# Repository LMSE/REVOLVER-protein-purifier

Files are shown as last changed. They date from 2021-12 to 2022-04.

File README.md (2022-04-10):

# REVOLVER: An automated protein purification system

<p align="center">
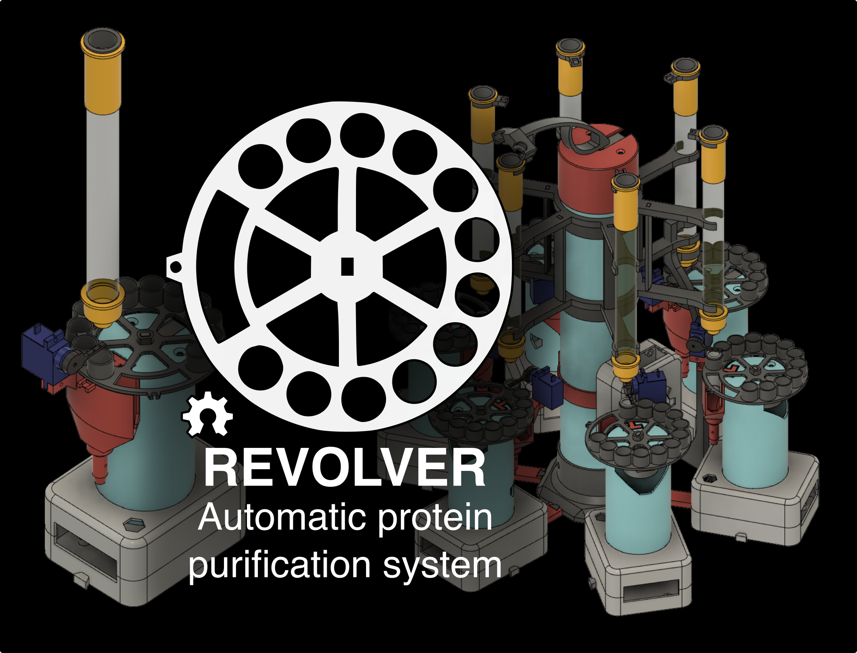
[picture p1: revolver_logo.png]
  
</p>

This repository contains all the hardware and firmware files to build and operate REVOLVER: an automated protein purifier based on paralleled large-scale gravity-column workflows. We also present MULTIVOLVER, a multiplexed version of REVOLVER that allows for simultaneous purification of up to six samples at a time.

REVOLVER was developed by Patrick Diep and Jose L. Cadavid at the University of Toronto. A full and detailed description of our system has been published in HardwareX and can be found [here](https://doi.org/10.1016/j.ohx.2022.e00291).

## Contents of repository

This repository contains all files necessary to print, build, and operate REVOLVER. It is divided in three main sections:

### Electronics

This folder contains the schematics for wiring the components of REVOLVER to an Arduino Nano board. This schematic was used to create a custom PCB using [EasyEDA](https://easyeda.com/) that was then ordered through [JLCPCB](https://jlcpcb.com/). The PCB file is included as a Gerber file that can be used to directly order a copy of the PCB (two PCBs fit a 10x10 cm panel). We additionally include a .json version of the PCB that can be opened with EasyEDA.

The raw PCB project can be accessed through [OSHWLab](https://oshwlab.com/JoseLCadavid/fractioncollector). If you would like to make your own PCB, please clone the project first and proceed with your improvements. Our current PCB corresponds to V2 in the project page.

### Firmware

This folder contains the Arduino firmware for configuring REVOLVER in single mode (single_sampler) or in MULTI-VOLVER mode (distributor_device and revolver_device). To upload (flash) the firmware to an Arduino board, you'll need a recent version of the Arduino IDE that can be found [here](https://www.arduino.cc/en/software). You can follow [this](https://www.arduino.cc/en/Tutorial/getting-started-with-ide-v2/ide-v2-uploading-a-sketch) tutorial on how to upload the firmware.

REVOLVER uses code and libraries written by other users and we would like to acknowledge them here:

* Serial communication and parser: This routine is based on [this](https://forum.arduino.cc/t/serial-input-basics-updated/382007/8) excellent tutorial by user **Robin2** on the Arduino forums.

* I2C bus scanner: This function is based on [this](https://playground.arduino.cc/Main/I2cScanner/) code.

Additionally, our code relies on these libraries:

* [Stepper](https://www.arduino.cc/en/reference/stepper/): For controlling stepper motors.
* [Servo](https://www.arduino.cc/reference/en/libraries/servo/): For controlling servos.
* [Wire](https://www.arduino.cc/en/reference/wire): For handling I2C communication.

Please verify that your Arduino IDE has access to these libraries before uploading the firmware to the Arduino boards. You can follow [this](https://www.arduino.cc/en/Guide/Libraries) tutorial for more information on how to do so. Detailed instructions on operating REVOLVER can be found in our manuscript.

### Hardware

This folder contains the STL files for all the 3D-printed parts required for REVOLVER and MULTI-VOLVER. These parts can be printed with no supports using any FDM printer with a size similar to that of an Ender 3; we've printed all our parts in PLA. We also included the f3d files that can be edited using Fusion 360 in case you'd like to customize the system even more. The bill of materials (BOM) is also included as a spreadsheet with some useful links to purchase parts.

## Building and using REVOLVER

The instructions for setting up and using REVOLVER are given in more detail in our manuscript. REVOLVER is controlled via serial commands, so any computer with a working USB connector and an installation of the Arduino IDE is required.

If you experience any issues when using our system, or otherwise have other suggestions, please create an issue and we are happy to help as soon as we can. Note that our manuscript includes a guide to troubleshooting common problems, so please check it out before posting.

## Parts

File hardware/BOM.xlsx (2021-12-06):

Designator | Components | Cost per package - CAD | Items per package | Items per REVOLVER | Total cost per REVOLVER (CAD) | Items per 3-device MULTIVOLVER | Total cost per 3-device MULTIVOLVER (CAD) | Items per 6-device MULTIVOLVER | Total cost per 6-device MULTIVOLVER (CAD) | Material Source | Material type
PURCHASED IN SETS
Servo | SG90 servo motor | $18.00 | 5 | 1 | $3.60 | 4 | $14.40 | 4 | $14.40 | https://www.amazon.ca/gp/product/B07Z16DWGW/ref=ppx_yo_dt_b_asin_title_o08_s00?ie=UTF8&psc=1 | Electronic Component
Servo horn | Single-sided horn for SG90 servo motor |  |  |  | cost included above |  | cost included above |  | cost included above | https://www.amazon.ca/gp/product/B07Z16DWGW/ref=ppx_yo_dt_b_asin_title_o08_s00?ie=UTF8&psc=1 | Metal
6 mm phillips screw | 6 mm phillips screw |  |  |  | cost included above |  | cost included above |  | cost included above | https://www.amazon.ca/gp/product/B07Z16DWGW/ref=ppx_yo_dt_b_asin_title_o08_s00?ie=UTF8&psc=1 | Metal
Stepper | 28BYJ-48 stepper motor with ULN2003 driver board | $20.00 | 5 | 1 | $4.00 | 3 | $12.00 | 3 | $12.00 | https://www.amazon.ca/gp/product/B087B5NWY4/ref=ppx_yo_dt_b_asin_title_o00_s00?ie=UTF8&psc=1 | Electronic Component
Stepper driver | ULN2003 (DIP-16L) Darlington array |  |  |  | cost included above |  | cost included above |  | cost included above | https://www.amazon.ca/gp/product/B087B5NWY4/ref=ppx_yo_dt_b_asin_title_o00_s00?ie=UTF8&psc=1 | Electronic Component
HARDWARE
PLA filament | EconoFil™ PLA 3D printer filament (assorted colours) | $25.00 | 1 | 0.3 | $7.50 | 0.6 | $15.00 | 0.95 | $23.75 | www.filaments.ca | PLA | kg
PVC pipe | PVC pipe | $33.44 | 5 | 0 | 0 | 1 | $6.69 | 1 | $6.69 | https://www.mcmaster.com/48925K99/ | PVC | ft
12 mm M3 screw | 12 mm M3 screw | $1.50 | 4 | 2 | $0.75 | 9 | $3.38 | 15 | $5.62 | https://www.creatroninc.com/product/12mm-m3-machine-screw-4-pack/ | Metal
6 mm M3 screw | 6 mm M3 screw | $1.50 | 4 | 4 | $1.50 | 16 | $6.00 | 28 | $10.50 | https://www.creatroninc.com/product/6mm-m3-tapper-machine-screw-4-pack/ | Metal
M3 nut | M3 nut | $1.00 | 4 | 2 | $0.50 | 9 | $2.25 | 15 | $3.75 | https://www.creatroninc.com/product/m3-nut-4-pack/ | Metal
Small tubing | Nalgene™ 489 Linear LDPE Tubing (8010-0125) | $100.00 | 100 | 10 | $10.00 | 12 | $12.00 | 15 | $15.00 | https://www.thermofisher.com/order/catalog/product/8010-0125 | LDPE | ft
Large tubing | Nalgene™ Non-Phthalate PVC Tubing (8701-4060) | $279.00 | 100 | 1 | $2.79 | 1.5 | $4.18 | 2 | $5.58 | https://www.thermofisher.com/order/catalog/product/8701-0010 | PVC | ft
1-way valve | Check Valve, Female Luer Lock Inlet, Barbed Outlet | $0.78 | 1 | 2 | $1.56 | 2 | $1.56 | 2 | $1.56 | https://www.qosina.com/check-valve-white-inlet-clear-outlet-female-luer-lock-barbed-80505 | Plastic
Valve adaptor | Male Luer with Spin Lock to Barb | $0.65 | 1 | 2 | $1.30 | 2 | $1.30 | 2 | $1.30 | https://www.qosina.com/male-luer-with-spin-lock-to-barb-89341 | Plastic
Tube connector | Hose tubing connectors, straight, conical nozzles (5-7 mm) | $9.98 | 10 | 7 | $6.99 | 10 | $9.98 | 13 | $12.97 | https://www.buerkle.de/en/hose-tubing-connectors-straight-conical-nozzles#similar | Plastic
Y Connector | Y Connector, Barbed, Natural | $1.58 | 1 | 0 | $0.00 | 3 | $4.74 | 5 | $7.90 | https://www.qosina.com/Y-Connector-Barbed-Natural-61628 | Plastic
ELECTRONICS
Prototyping board | 3cm x 7cm double-sided prototyping board | $2.80 | 1 | 1 | $2.80 | 1 | $2.80 | 2 | $5.60 | https://www.creatroninc.com/product/3-x-7cm-double-side-fr4-prototyping-board/ | Electronic Component
Headers (male/female) | Header connector (male header, female header) | $10.99 | 20 | 2 | $1.10 | 8 | $4.40 | 14 | $7.69 | https://www.amazon.ca/Neuftech-2-54mm-Single-Header-cannector/dp/B00QHS1IYG?s=hi | Electronic Component
Power block | Screw Terminal Block | $1.50 | 1 | 1 | $1.50 | 1 | $1.50 | 1 | $1.50 | https://www.creatroninc.com/product/2p-screw-terminal-block-0-2-2/ | Electronic Component
DC pumps | 12V DC pumps | $13.98 | 1 | 3 | $41.94 | 3 | $41.94 | 3 | $41.94 | https://www.amazon.ca/Gikfun-Aquarium-Cooled-Diaphragm-EK1856C/dp/B0744DL1S9 | Electronic Component
Nano | Arduino Nano | $28.00 | 5 | 1 | $5.60 | 4 | $22.40 | 7 | $39.20 | https://www.amazon.ca/gp/product/B0816SGKHH/ref=ppx_yo_dt_b_asin_title_o09_s00?ie=UTF8&psc=1 | Electronic Component
Hall sensor | A3144 hall effect sensor | $13.00 | 20 | 2 | $1.30 | 6 | $3.90 | 12 | $7.80 | https://www.amazon.ca/Effect-Sensor-A3144-A3144E-OH3144E/dp/B07QNX6HWT | Electronic Component
Magnet | 3x2mm round magnet | $14.00 | 150 | 1 | $0.09 | 6 | $0.56 | 12 | $1.12 | https://www.amazon.ca/Magnets-Refrigertor-Whiteboard-Durable-Multi-Use/dp/B07C9FDR7V | Electronic Component
Jumper (FM) | Jumper wires (FM) | $5.95 | 40 | 10 | $1.49 | 25 | $3.72 | 40 | $5.95 | https://www.creatroninc.com/product/40-pin-m-f-splittable-jumper-wire/ | Electronic Component
Jumper (MM) | Jumper wires (MM) | $5.95 | 40 | 5 | $0.74 | 10 | $1.49 | 15 | $2.23 | https://www.creatroninc.com/product/40-pin-m-m-splittable-jumper-wire/ | Electronic Component
Jumper (FF) | Jumper wires (FF) | $5.95 | 40 | 5 | $0.74 | 10 | $1.49 | 15 | $2.23 | https://www.creatroninc.com/product/40-pin-f-f-splittable-jumper-wire/ | Electronic Component
Alligators | Alligator to Jumper wires (assorted M and F ends) | $6.50 | 10 | 6 | $3.90 | 6 | $3.90 | 6 | $3.90 | https://www.creatroninc.com/product/alligator-to-jumper-cable-10-pack/ | Electronic Component
Hookup wire | 22AWG Hookup Wire (Black) | $4.75 | 1 | 0.2 | $0.95 | 0.5 | $2.38 | 1 | $4.75 | https://www.creatroninc.com/product/22awg-hookup-wire-black/ | Electronic Component
Power supply | Variable voltage power supply | $27.99 | 1 | 2 | $55.98 | 2 | $55.98 | 2 | $55.98 | https://www.amazon.ca/gp/product/B083W5HC37/ref=ppx_yo_dt_b_asin_title_o04_s00?ie=UTF8&psc=1 | Electronic Component
16-pin socket | 16 pin DIP IC socket | $0.39 | 1 | 1 | $0.39 | 3 | $1.17 | 6 | $2.34 | https://www.pcboard.ca/16-pin-ic-socket-narrow | Electronic Component
MOSFET | IRF520 N-channel MOSFET | $2.00 | 1 | 2 | $4.00 | 2 | $4.00 | 2 | $4.00 | https://www.creatroninc.com/product/irf520-n-channel-mosfet-100v-9-7a/ | Electronic Component
10 kOhm resistor | 10 kOhm resistor | $0.25 | 10 | 2 | $0.05 | 2 | $0.05 | 2 | $0.05 | https://www.creatroninc.com/product/1-4w-assorted-resistor-kit/ | Electronic Component
1N4006 diode | 1N4007 rectifier diode | $1.00 | 4 | 2 | $0.50 | 2 | $0.50 | 2 | $0.50 | https://www.creatroninc.com/product/1n4007-1000v-1a-rectifier-diode-4-pack/ | Electronic Component
10 uF capacitor | 10 uF radial electrolytic capacitor | $0.45 | 2 | 1 | $0.23 | 4 | $0.90 | 7 | $1.57 | https://www.creatroninc.com/product/electrolytic-capacitor/ | Electronic Component
PCB | Printed circuit board | $15.00 | 10 | 1 | $1.50 | 4 | $6.00 | 7 | $10.50 | https://jlcpcb.com/?href=easyeda-home | Electronic Component
 |  |  |  | TOTAL | $165.29 | TOTAL | $252.54 | TOTAL | $319.89
TOOLS
Put in Captions
Gravity column | Glass chromatography column | $128.00 | 2 | 1 | $64.00 | 3 | $192.00 | 6 | $384.00 | https://www.bio-rad.com/fr-ca/sku/7371517-econo-column-chromatography-columns-1-5-15-cm?ID=7371517 | Composite
** mention: 1 power supply can be removed if PCB is desgined to control a third pump
 |  |  |  |  | REVOLVER | 3-device MULTI-VOLVER | 6-device MUTLI-VOLVER
 |  |  |  | Hardware | $40.49 | $88.11 | $112.50
 |  |  |  | Electronics | $124.80 | $159.06 | $198.86

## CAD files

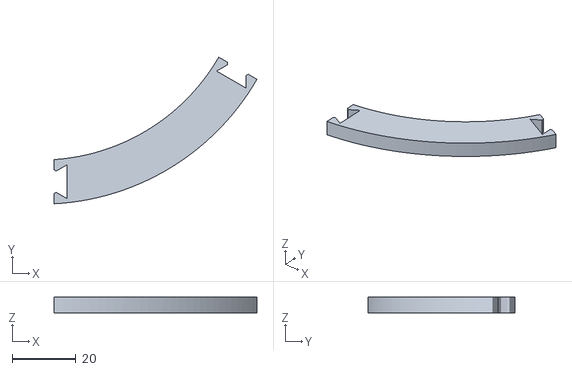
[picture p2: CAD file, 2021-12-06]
hardware/STL/multivolver_linker_long.stl
63.9 x 46.2 x 5.00

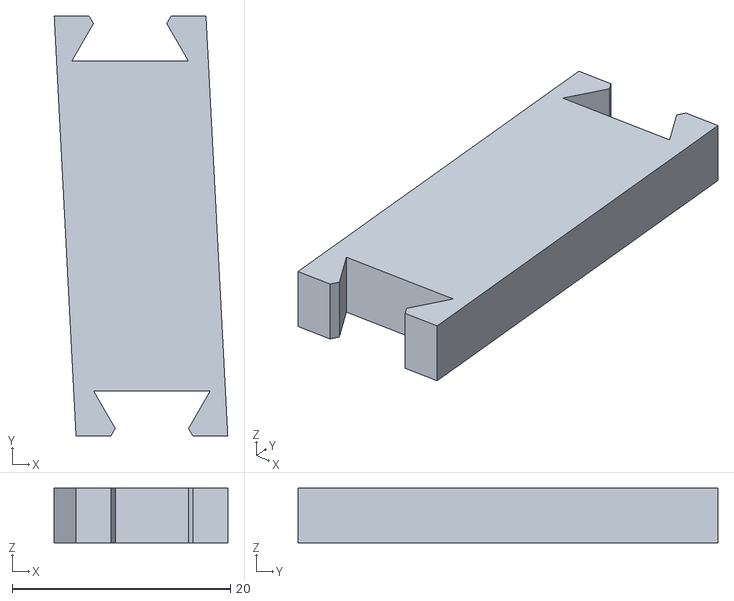
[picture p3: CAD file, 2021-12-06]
hardware/STL/multivolver_linker_short.stl
15.9 x 38.5 x 5.00

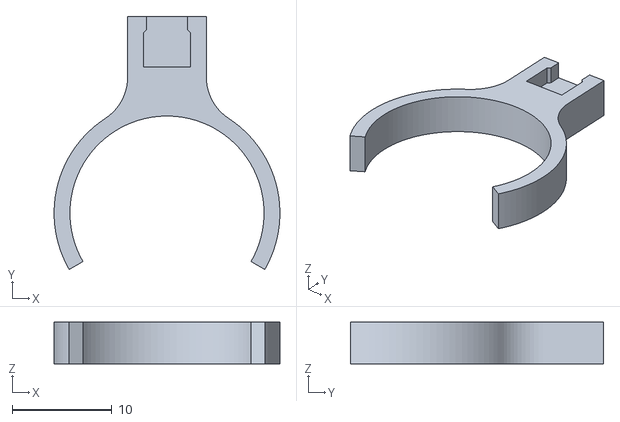
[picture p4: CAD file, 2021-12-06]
hardware/STL/multivolver_hall_ring.stl
22.7 x 25.4 x 4.20

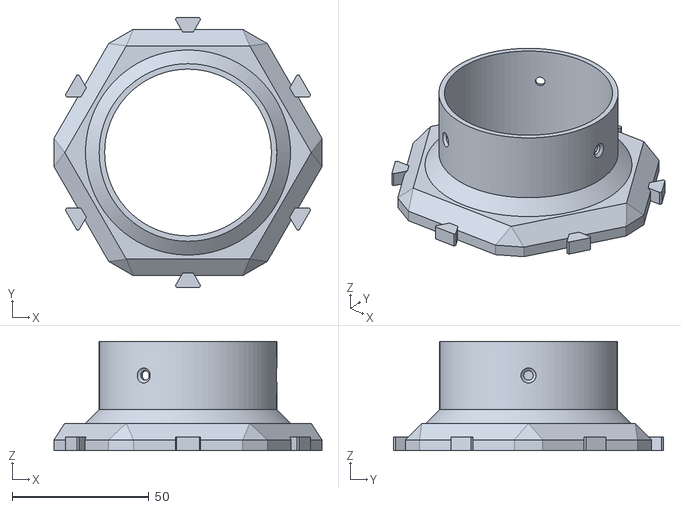
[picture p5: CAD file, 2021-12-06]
hardware/STL/multivolver_base.stl
97.9 x 98.7 x 40.0

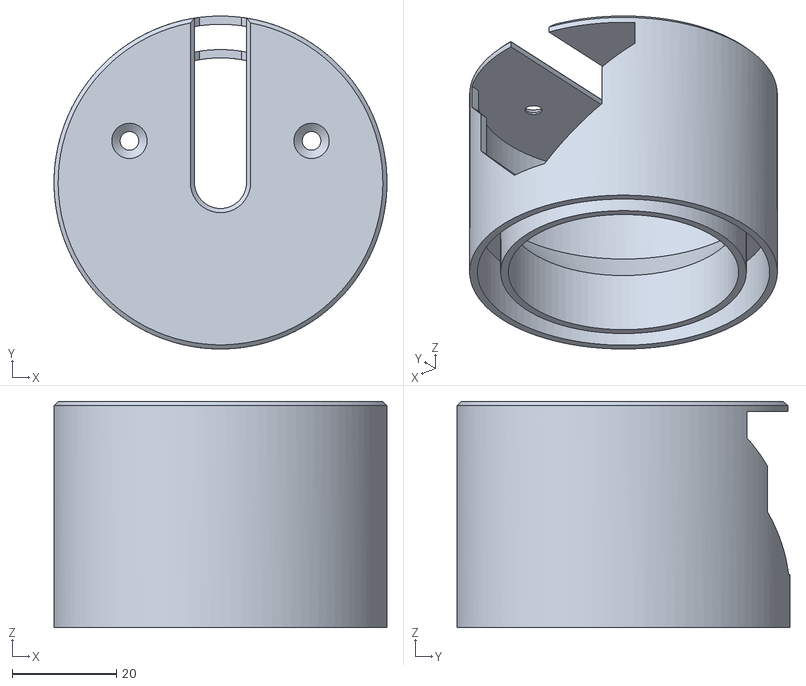
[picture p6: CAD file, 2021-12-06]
hardware/STL/multivolver_top.stl
64.0 x 64.0 x 43.5

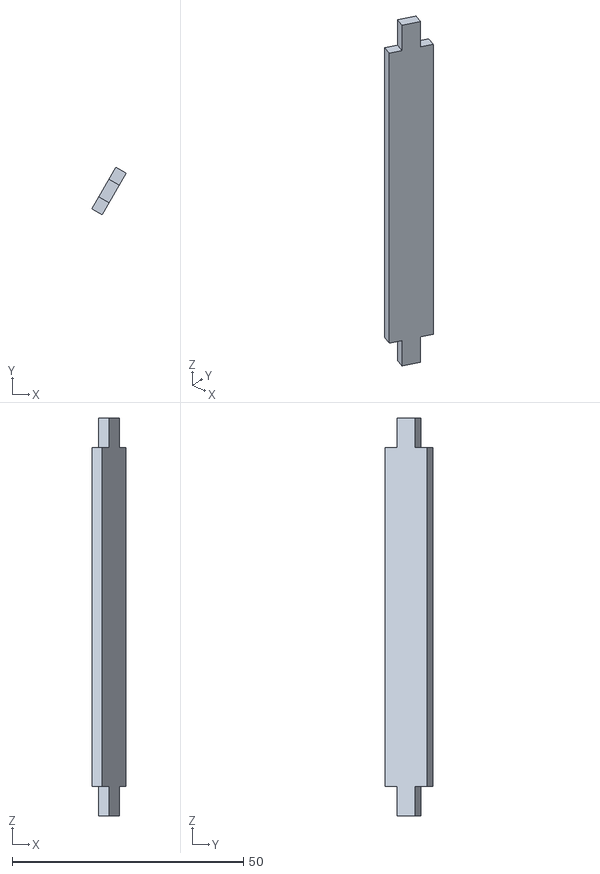
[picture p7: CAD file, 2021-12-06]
hardware/STL/multivolver_gripper_post.stl
7.45 x 10.3 x 86.0

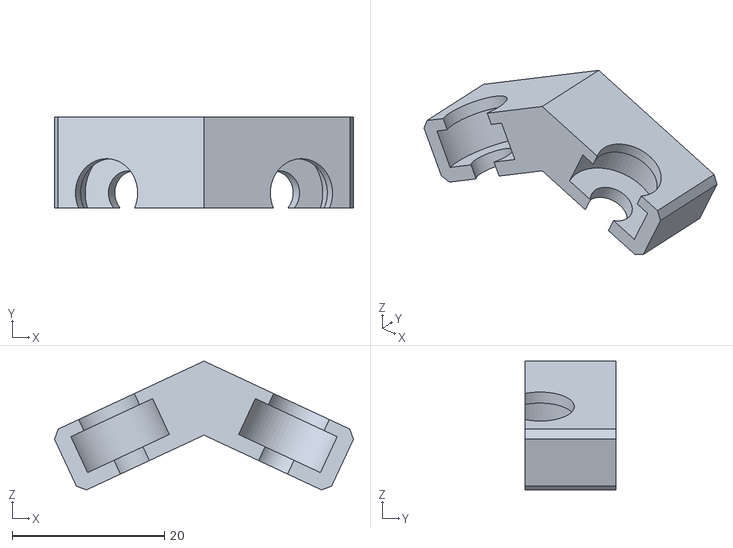
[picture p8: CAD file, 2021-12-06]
hardware/STL/multivolver_arm_head.stl
39.2 x 12.0 x 16.9

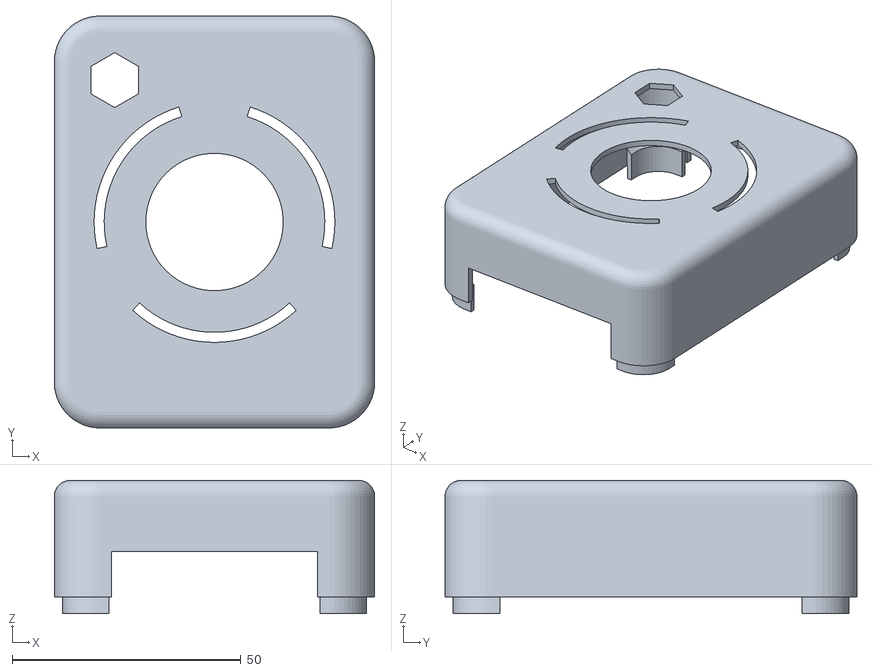
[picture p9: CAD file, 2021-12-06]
hardware/STL/revolver_box_top.stl
70.0 x 90.0 x 29.1

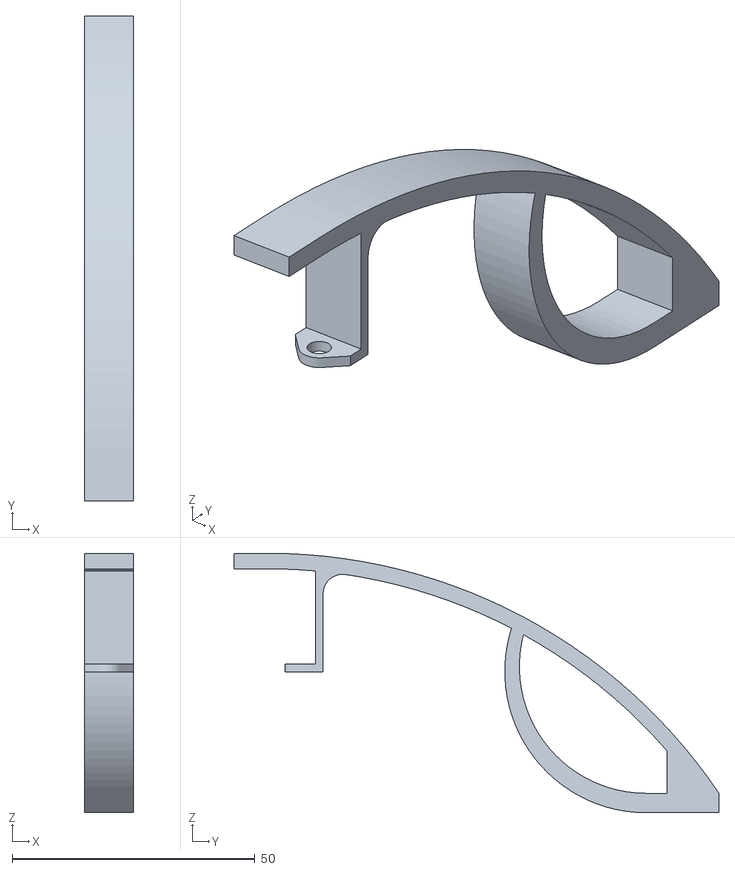
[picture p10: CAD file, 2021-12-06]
hardware/STL/multivolver_distributor_arm.stl
10.0 x 99.8 x 53.4

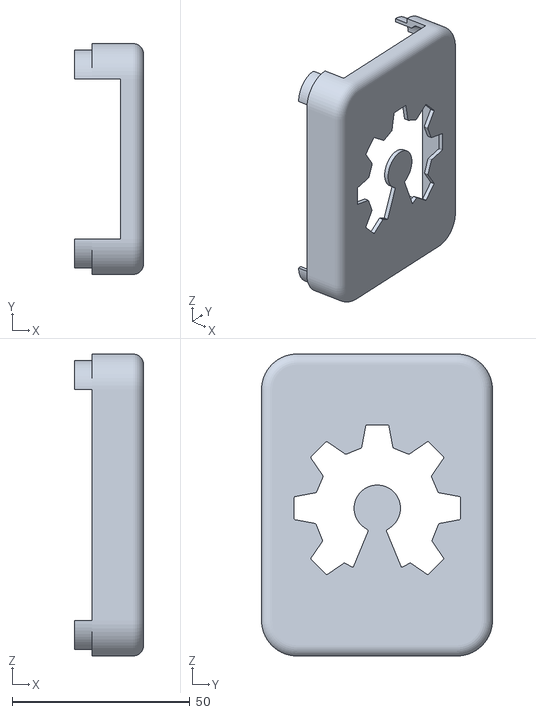
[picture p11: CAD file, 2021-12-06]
hardware/STL/multivolver_box_top.stl
19.5 x 65.0 x 85.0

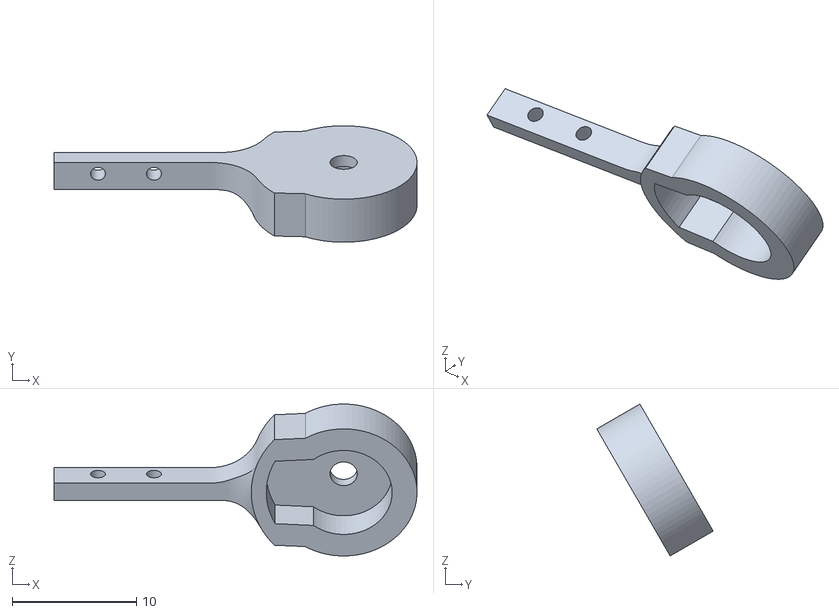
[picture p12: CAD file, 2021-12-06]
hardware/STL/revolver_servo_arm.stl
29.2 x 9.36 x 12.2

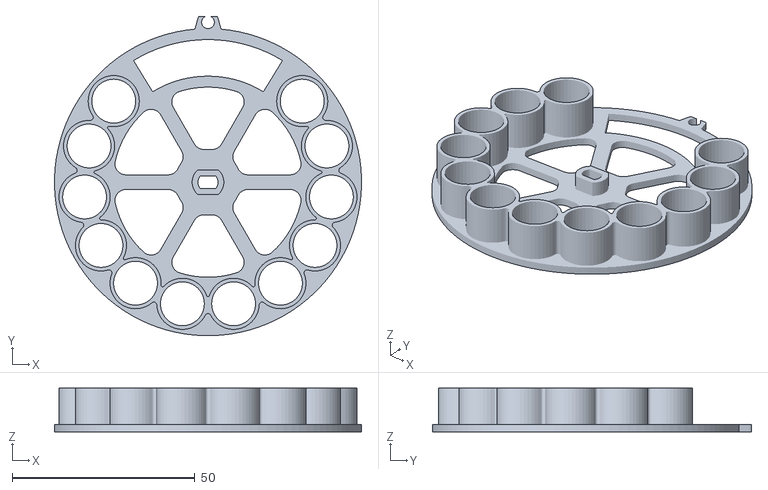
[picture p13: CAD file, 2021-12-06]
hardware/STL/revolver_plate.stl
84.0 x 87.3 x 12.0

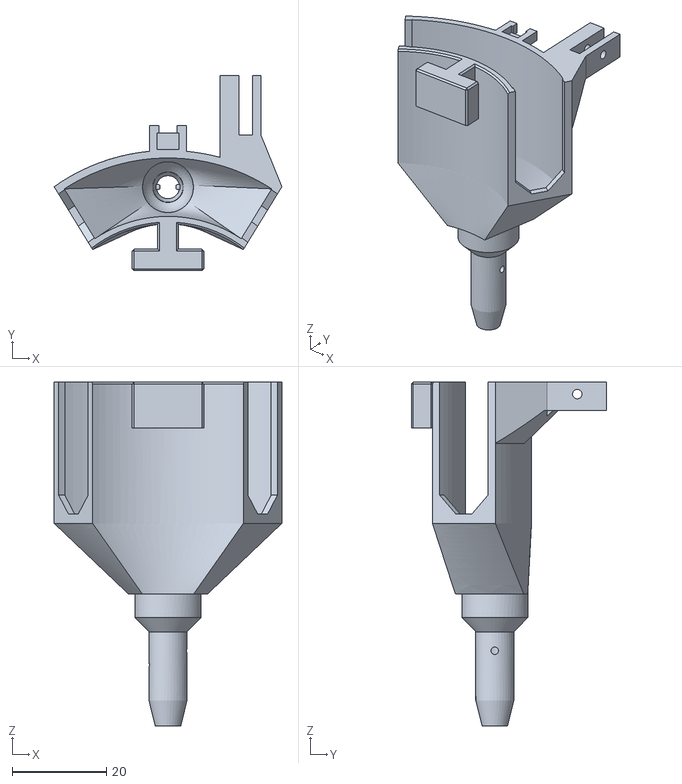
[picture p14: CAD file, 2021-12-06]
hardware/STL/revolver_waste_collector.stl
48.3 x 41.5 x 73.0

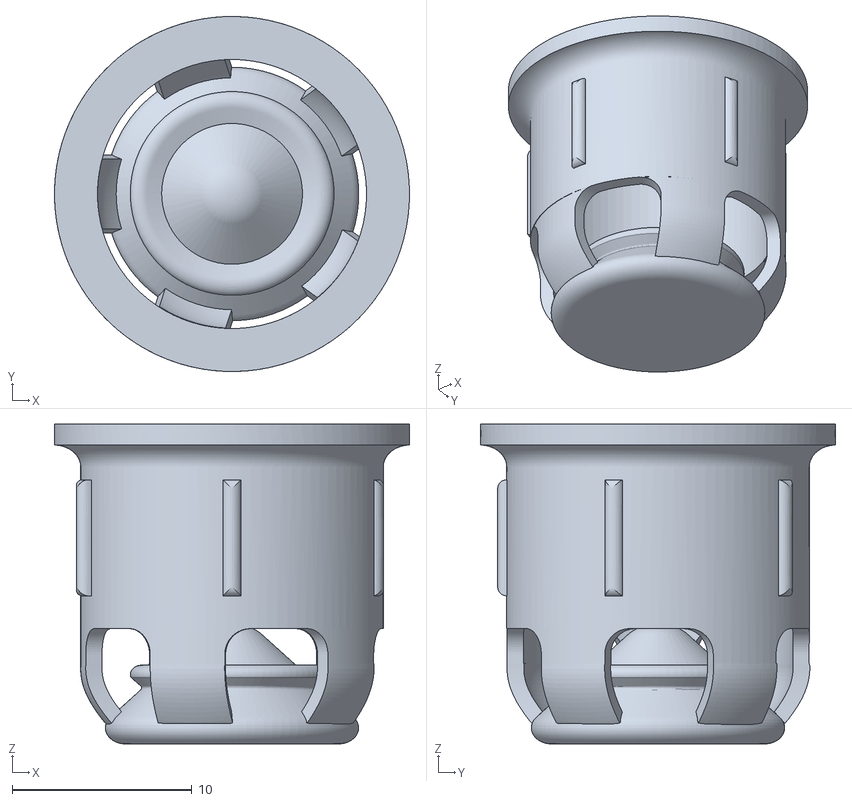
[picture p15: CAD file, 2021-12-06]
hardware/STL/revolver_flow_distributor.stl
19.8 x 19.8 x 17.8

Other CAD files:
hardware/STL/multivolver_box_bottom.stl
hardware/STL/revolver_waste_collector_syphon.stl
hardware/STL/revolver_tower.stl
hardware/STL/multivolver_box_mount.stl
hardware/F3D files/REVOLVER separator.f3d
hardware/STL/multivolver_column_gripper.stl
hardware/STL/revolver_box_bottom.stl
hardware/STL/revolver_column_grip.stl

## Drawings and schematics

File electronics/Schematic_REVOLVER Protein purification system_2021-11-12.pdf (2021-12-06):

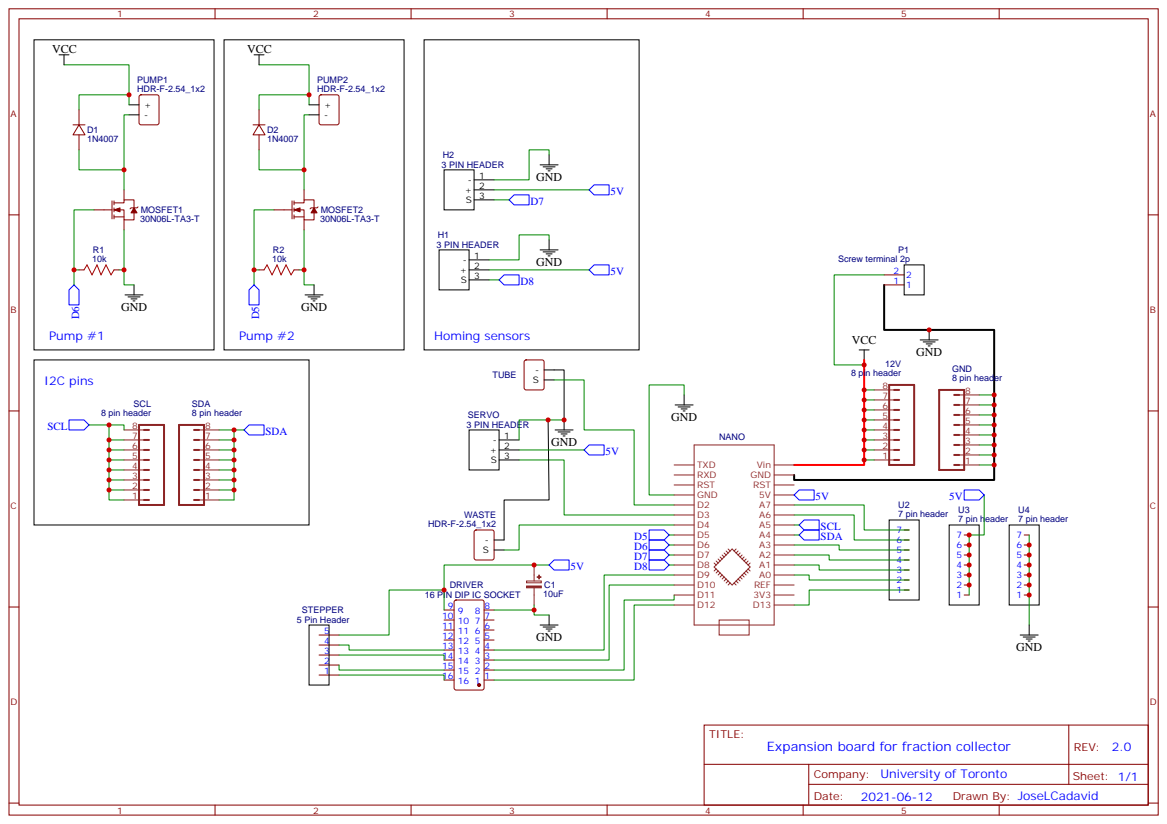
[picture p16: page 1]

Company: University of Toronto

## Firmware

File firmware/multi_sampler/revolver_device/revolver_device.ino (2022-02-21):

/*
Arduino code for running the sample collection from a chromatography process with a single collector.
Instructions set via serial connection and sent to distributors
----------------
Worker device (i.e. Revolver)
*/

// Include libraries
#include <Stepper.h> // For driving stepper motor (28byj-48)
#include <Servo.h>  // For driving the microservo (SG90)
#include <Wire.h> // For I2C communication - not needed for single device

// I2C address: Make sure each board gets a unique address and write it down on the revolver
const byte I2CAddress = 1; // this should be an integer between 1 and 127
// Define the type of collector (1 for normal, 2 for siphon version)
byte collectorType = 1;

// Define pins - these are meant to work with an Arduino Nano, but should also work with an Arduino Uno
const byte tubeSensor = 2; // Level sensor in eppi tubes
const byte servoPin = 3; // Servo
const byte wasteSensor = 4; // Liquid sensor for waste funnel
const byte pump1 = 5; // Pump#1 - pumps not needed when running in multiplexed device
const byte pump2 = 6; // Pump #2 - pumps not needed when running in multiplexed device
const byte dockingSensor = 7; // For docking the distributor to the device - not needed for single device
const byte homeSensor = 8; // For homing the revolving plate (hall effect sensor A3144)
const byte motPins[] = {9, 10, 11, 12}; // Pins for stepper motor

// Declare variables

/* Constant properties of the hardware */
#define STEPS  32   // Number of steps per revolution of internal shaft of a 28byj-48 stepper
const float angleTubes = 23.8; // angular separation between tubes in degrees
const float angleWaste = 43.3; // angle between the center of the waste collector and the center of the first tube
volatile byte nTubes = 5; // Number of tubes in the sampler - default 5, bu can be modified
// Other variables
byte sensorValue; // Value of the level sensor attached to the servo
byte wasteValue = HIGH; // Value of the liquid sensor in waste collector - default HIGH = not triggered
int numWashes = 1; //Number of washes
int nSteps;  // 2048 = 1 Revolution
bool washDone; // Logical value indicating whether the wash solution has completely left the column
unsigned long timeOff = 0; // time that the waste collector is empty
unsigned long currentMillis; // current time in milliseconds
const unsigned long timeEmpty = 20000; // time in milliseconds the waste container must be empty before accepting wash is done
const unsigned long timeMin = 5000; // Minimum time in milliseconds to spend in each microfuge tube
const unsigned long timeMaxTube = 60000; // Maximum time in millseconds that we'll wait for each tube before showing a warning
bool sendError = false; // flag to indicate if we get the distributor to display an error message

// Variables for parsing I2C communication
char messageFromMaster; // Character describing the instruction to execute
const byte nArgs = 3; // Maximum number of arguments to be used in functions
unsigned int args[nArgs]; // arguments for executing the functions. Declared as unsigned to be able to store larger numbers if needed
boolean taskDone = true; // variable to indicate if a given task is done. Starts as true to receive first instruction
boolean newTask = false;

// Define objects
// Setup of proper sequencing for Motor Driver Pins: In1, In2, In3, In4 in the sequence 1-3-2-4
Stepper plateStepper(STEPS, motPins[0], motPins[2], motPins[1], motPins[3]);
Servo   levelServo;

/* Run this program once*/
void setup(){

  // ========== Setup pins and monitor ========================================

  // Join I2C bus
  Wire.begin(I2CAddress);
  // Register events
  Wire.onReceive(receiveEvent);
  Wire.onRequest(requestEvent);

  // Define pin modes
  pinMode(tubeSensor, INPUT_PULLUP);
  pinMode(wasteSensor, INPUT_PULLUP);
  pinMode(pump1, OUTPUT);
  pinMode(pump2, OUTPUT);
  pinMode(dockingSensor, INPUT_PULLUP);
  pinMode(homeSensor, INPUT_PULLUP);
  pinMode(LED_BUILTIN, OUTPUT);
  digitalWrite(LED_BUILTIN, LOW);

  // Turn off motor coils
  for (int i; i<4; i++){ digitalWrite(motPins[i], LOW);}
  plateStepper.setSpeed(700);
  // Attach servo and raise for homing
  levelServo.attach(servoPin);
  levelServo.write(90);

}

/* Loop function - listen to I2C bus */
void loop(){
  // Execute commands given by serial to the distributor and sent via I2C to revolver
  if (newTask){
    digitalWrite(LED_BUILTIN, HIGH); // LED for debugging
    newTask = false;
    executeCommand();
    // Once task is completed
    taskDone = true;
    digitalWrite(LED_BUILTIN, LOW);
  }
}

// ====================================================
// Functions for I2C

// Once a task is done, we inform the distributor, who sends a new command
void receiveEvent(int howMany){
  // Read data in I2C bus - the distributor will send 4 bytes:
  // a character with the instruction, and three ints as arguments
  messageFromMaster = Wire.read(); // receive byte 1 as a character. When we read, we evacuate one byte
  for (int i = 0; i < nArgs; i++){
    args[i] = Wire.read();
  }
  // Reset task
  taskDone = false;
  // Indicate new task is received
  newTask = true;
}

// Executed when there is a request. For now only indicate if task is done (1) or not (0)
// The auto homing routine also requests one byte for the hall effect sensor, so we include that
// as another message
void requestEvent(){
  byte docked = digitalRead(dockingSensor); // Read docking hall effect
  if (sendError){
    // Display error message, takes precedence over anything else
    Wire.write(3);
    // Reset error flag
    sendError = false;
  }
  else {
    // No error message, look at whether the tasks are done
    if (taskDone && docked == LOW){
      Wire.write(2);
    }
    else if (taskDone && docked == HIGH){
      Wire.write(1);
    }
    else {
      Wire.write(0);
    }
  }
}

void executeCommand(){
  // Call the required command
  // All commands have a different letter so we only
  // need their first character to identify them
    char firstLetter = messageFromMaster; // in the single version, this is messageFromPC[0]. We need to reconcile these and add them as an argument
    switch (firstLetter){
    case 'H': // Auto Home
      homePlate();
      break;
    case 'F': // Fill tubes
      // override number of tubes if argument was given
      if (args[0] > 0){
        nTubes = args[0];
      }
      fillTubes();
      break;
    case 'C': // Collect waste
      collectWaste(); // No arguments, but could take an optional argument from args that is the wait time
      break;
      // TO DO - add a case for "settings" where we modify waiting times and things like that
    case 'R': // Rotate manually
      rotatePlate();
      break;
  }

}

// ====================================================
// Functions for running the protocol

// Home the plate
void homePlate(){
  // Step counter for finding homing position
  int posSteps = 0;
  // Lift servo
  levelServo.write(90);
  delay(500);
  // Rotate back a bit (approx 30 degrees) just in case we have started on top of the sensor
  plateStepper.step(-180);
  // Start rotating plate until sensor is triggered
  while (digitalRead(homeSensor) == HIGH){
    plateStepper.step(2); // 2 steps at a time, could be tuned though
    posSteps = posSteps + 2; // update position
    // If we go around once without finding the sensor, we stop and throw a notification
    // this prevents infinite loops if the sensor is not installed
    if (posSteps > 2100){
      return;
    }
  }
  // Reset step counter
  posSteps = 0;
  // Rotate more until the sensor is no longer triggered
  while (digitalRead(homeSensor) == LOW){
    plateStepper.step(2);
    posSteps = posSteps + 2;
  }
  // Now we found the positions (step indices) where the sensor is triggered.
  // we take the half point, so we go back half the steps between the limits
  plateStepper.step(-round(posSteps/2));
}

// Function for collecting waste after washes
void collectWaste(){
  int washDone = false;
  sendError = false;
  // Wait until the sensor is triggered the first time before we start counting.
  // If it's not triggered within a certain time, it might be that the user forgot to add lysate,
  // so we trigger an error flag
  currentMillis = millis();
  while (wasteValue == HIGH){
    wasteValue = digitalRead(wasteSensor);
    delay(10);
    if (millis() - currentMillis >= timeEmpty){
      // Trigger error flag. Will be reset once the distributor asks the status
      // of the REVOLVER
      sendError = true;
      // Reset timer
      currentMillis = millis();
    }
  }
  // In case there was an error and it was resolved, reset error flag
  sendError = false;

  // Handle the waste collection depending on the type of collector
  switch (collectorType){
    // Version 1 of collector - exit criterion is that the collector remains empty
    case 1:
      // Get current time
      currentMillis = millis();
      while (!washDone){
        wasteValue = digitalRead(wasteSensor);
        if (wasteValue == LOW){
          // Reset timer: Sensor triggered, there is liquid in waste collector.
          currentMillis = millis();
          timeOff = 0;
        }
        else{
          // Increase time counter: No liquid detected.
          timeOff = millis() - currentMillis;
        }
        // Has the collector been empty for longer than the threshold time?
        //Return FALSE if timeOff does not exceed threshold seconds.
        washDone = (timeOff >= timeEmpty);
        delay(10);
      }
      break;
    // Version 2 of collector (siphon) - exit criterion is that the collector signal
    // stops changing (i.e. stays full OR empty)
    case 2:
    // Get current time and read initial state of sensor
    currentMillis = millis();
    byte wasteValueOld = digitalRead(wasteSensor);
    while (!washDone){
      // Read sensor
      wasteValue = digitalRead(wasteSensor);
      if (wasteValue != wasteValueOld){
        // Reset timer: Liquid content in the siphon changed
        currentMillis = millis();
        timeOff = 0;
      }
      else{
        // Increase time counter: Siphon state is unchanged
        timeOff = millis() - currentMillis;
      }
      // Update old state
      wasteValueOld = wasteValue;
      // Has the collector been empty for longer than the threshold time?
      //Return FALSE if timeOff does not exceed threshold seconds.
      washDone = (timeOff >= timeEmpty);
      delay(10);
    }
    break;
  }

  delay(2000);

}
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

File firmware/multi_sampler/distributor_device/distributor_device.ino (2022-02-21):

/*
Arduino code for running the sample collection from a chromatography process with a single collector.
Instructions set via serial connection and sent to distributors
----------------
Distributor device
*/

// V1 - I2C scanner based on code from https://playground.arduino.cc/Main/I2cScanner/
// Include libraries
#include <Wire.h>
#include <Stepper.h>

// Calibration factors for pumps (to convert mL to time)
const float smallVolumeCalibrationPump1 = 1.00;
const float largeVolumeCalibrationPump1 = 1.00;
const float smallVolumeCalibrationPump2 = 1.00;
const float largeVolumeCalibrationPump2 = 1.00;

// Define pins - distributor only has a stepper motor and pumps
const byte pump1 = 6; // Pump#1
const byte pump2 = 5; // Pump #2
const byte motPins[] = {9, 10, 11, 12}; // Pins for stepper motor

/* Constant properties of the hardware */
#define STEPS  32   // Number of steps per revolution of internal shaft of a 28byj-48 stepper
const int steps2take = 2048; // number of steps of motor - 1 revolution (motor is geared)

// Variables for parsing serial communication
const byte numChars = 32; // this value could be smaller or larger, as long as it fits the largest expected message
char receivedChars[numChars];
char tempChars[numChars];        // temporary array for use when parsing
// variables to hold the parsed data
char messageFromPC[numChars] = {0};
byte ledInstruction = 0;
boolean newData = false;

// Variables for I2C scanner and I2C communication
byte error, address; // Variables for I2C scanner
byte nI2C; // number of connected devices via I2C
const byte nI2CMax = 10; // Maximum number of I2C devices we will allow to be connected
const byte nTaskMax = 20; // Maximum number of tasks to be stored - TODO: This could be tuned
const byte nArgs = 3; // Maximum number of arguments to be used in functions
byte listI2C[nI2CMax]; // array that holds the addresses of the I2C devices connected to the bus
int locationsI2C[nI2CMax]; // array that contains the angular locations (in n steps) of the connected I2C devices
int angularPos = 0; // angular position of the motor when we start...arbitrary location
byte taskIdx[nI2CMax]; // array for storing the task being currently executed by each revolver
char taskName[nTaskMax]; // array for storing the tasks to be executed by each revolver (e.g. "H", "P", "F")
unsigned int taskArgs[nTaskMax][nArgs]; // array for storing arguments (up to three) for each of the tasks
unsigned int args[nArgs]; // arguments for executing the functions that are called manually, or for ease of reading
boolean allStored = false; // variable indicating whether the full protocol has been parsed and stored
byte nTask = 0; // Number of tasks received. Works as a index. Byte should allow for 255 instructions which is plenty
byte messageFromRevolver = 0; // Temporary storage for message from revolvers
boolean allDone; // variable that stores whether all devices are finished. We can use this to allow more instructions without reseting the devices
byte requestedAddress; // variable to store an I2C address if there is a manual request (e.g. rotate a plate)
boolean storeTask = false; // Flag for storing upcoming instructions in an array

// Define objects
// Setup of proper sequencing for Motor Driver Pins: In1, In2, In3, In4 in the sequence 1-3-2-4
Stepper mainStepper(STEPS, motPins[0], motPins[2], motPins[1], motPins[3]);

/* Run this program once*/
void setup() {
  // ========== Setup pins and monitor ========================================
  // Start serial monitor
  Serial.begin(9600);
  // Join I2C bus as master (no address)
  Wire.begin();
  Serial.println("MULTIVOLVER: Parallel collection of chromatography fractions");

  // Define pin modes
  pinMode(pump1, OUTPUT);
  pinMode(pump2, OUTPUT);

  // Turn off motor coils
  for (int i; i < 4; i++){digitalWrite(motPins[i], LOW);}
  mainStepper.setSpeed(700);

  // Step 1: Only execute once - find number and addresses of connected I2C devices
  scanI2C();

  // Step 2: Rotate to get the location of the devices
  //locateI2C();
  Serial.println("Setup done...please locate devices");
}
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

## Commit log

2021-07-23 Initial commit single sampler code
2021-07-29 Establish serial to I2C data transfer and initial prototype
2021-07-31 Add function for manual rotation of device
2021-08-05 Fix error with pin number for pumps
2021-09-13 Initial commit of distributor device
2021-09-14 Update functions to match latest commit of single device
2021-09-25 Display time spent per tube collected
2021-09-25 Archive GUI prototype for future work
2021-10-13 Add auto locate devices with I2C
2021-10-13 Return docking sensor status
2021-11-12 Add STL files
    [multivolver_arm_head.stl, multivolver_base.stl, multivolver_box_bottom.stl, multivolver_box_mount.stl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]
2021-11-12 Add PCB files
2021-11-23 Add parameters to make calibration of pumps easier
2021-11-23 Add BOM
    [BOM.xlsx]
2021-12-06 Add f3d files
    [REVOLVER separator.f3d]
2021-12-06 Rename PCB file
2021-12-06 Add linkers for multi-volver
    [multivolver_linker_long.stl, multivolver_linker_short.stl]
2022-02-08 Add check to throw error message if collector or tubes don't trigger
2022-02-21 Tested error messages in Arduino
